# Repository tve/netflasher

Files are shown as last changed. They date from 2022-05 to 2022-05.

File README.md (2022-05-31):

NetFlasher2 - Emit a flash when a bird hits a net
================================================

The NetFlasher2 is a simple circuit to flash an LED when a bird hits a net and is used
in experiments to determine which window coverings are best to deter birds from flying
into them.

The netflasher detects when a bird hits a net using a vibration sensing switch.
It then briefly turns on a bright LED which is placed in the viewfield of a camera
recording the experiment.
This provides an unmistakable "hit" signal.

Instructions
------------

- Use micro-USB cable to power the netflasher (uses <80mA)
- The flashlight lights for 200ms when the vibration sensor is triggered
- After triggering, the flash is locked-out for 10s
- Tiny orange LED: slow (2s) = ready; fast (200ms) = 10s lock-out
- Red LED: vib sw detected (always active, even during lock-out)
- Green LED: display sensitivity (blink 1x/2x/3x/4x), 1=most, 4=least
- Blue sw:
  - first press: display sensitivity & reset lock-out
  - press again within 2s: change sensitivity (1/2/3/4)
- White sw next to microcontroller: program mode (cut power to exit)

Circuit Notes
-------------

### Net motion detector

- Vibration detection switch "SW-18010" https://www.adafruit.com/product/1766
- Sensitivity is adjusted by requiring toggles in multiple 10ms windows: sensitivity 1
  requires just one toggle, 2 requires toggles in 2x 10ms within 100ms of one-another,
  3 requires toggles in 2^2 = 4x 10ms intervals, 4 requires 8x 10ms intervals 

### Sensitivity switch

- Pushbutton to change sensitivity
- On-board sensitivity indicator LED (1, 2, 3, or 4 flashes)

### High power Cree LED

- Amber 5mm LED: C503B-ABS, 4430mcd @20mA, 40mA max continuous
- drive using 2N4401 w/82Ω -> ~40mA

### High power "flash" LED

(Not used due to size concerns)

- Wire-up raw flashlight LED
  - 135mA@2.8V=1/3W
  - 220mA@2.85V=0.6W
- 2N4401: 600mA max
  - resistor emitter-ground: 10Ω->1W flash
- On-board indicator LED
- To disassemble flashlight:
  - pull zoom ring hard and unscrew, remove driver
  - remove btn cap, punch btn through alum housing

Arduino
-------

To use `arduino-cli` install according to first post:
- https://forum.pjrc.com/threads/53548-Arduino-CLI-Alpha-Release-Teensy-Support
Instead of `arduino-cli core install teensy:avr` run:
- `arduino-cli core update-index`
- `arduino-cli core install teensy:arm`

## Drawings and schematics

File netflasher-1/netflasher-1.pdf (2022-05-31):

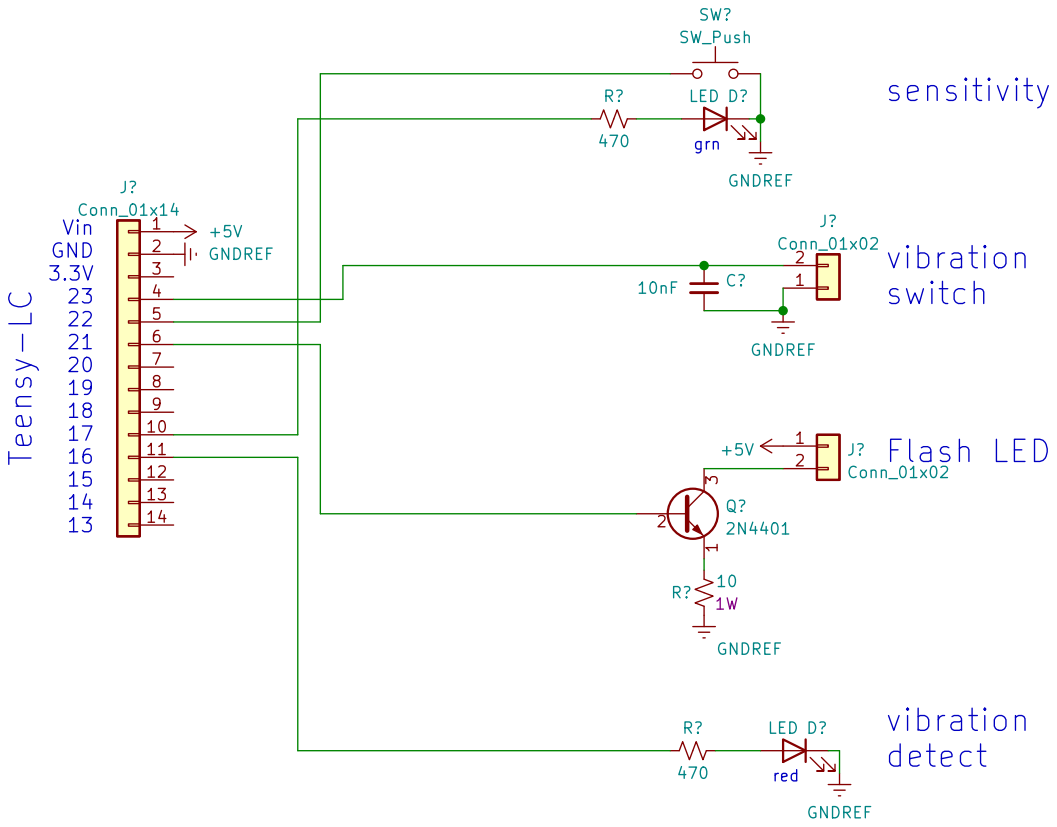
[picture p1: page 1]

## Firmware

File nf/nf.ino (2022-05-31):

#define codename "Net-Flasher"
#define codedate " 2022-0524 "

#include <EEPROM.h>
#include <Bounce.h>
typedef unsigned int u_int32;

const int vibSensePin = 23;
//Bounce vibSense = Bounce(vibSensePin, 10);
const int senseBtnPin = 22;
Bounce senseBtn = Bounce(senseBtnPin, 20);
const int flashEn = 21;
const int detectLed = 16;
const int senseLed = 17;
const int actLed = 13;
const int senseEE = 4;       // eeprom location
const int senseMax = 4;      // max vibration count value
const int flashDur = 200;    // flash duration in ms
int senseSet = 0;            // read from eeprom, vibration count setting
int senseCnt = 0;            // number of LED flashes to output (x2)
u_int32 senseAt = 0;         // last time the LED was updated
u_int32 senseBtnAt = 0;      // last time the button was pressed
volatile int vib = 0;        // set to 1 by interrupt handler
int vibCnt = 0;              // vibration count
int vibState = 0;            // digitalRead result

u_int32 flashAt = -60*1000;  // last time the flash was lit
u_int32 detectAt = -60*1000; // last time the detect LED was lit
u_int32 vibAt = 0;           // last time the detect LED was lit
u_int32 actAt = 0;           // last time the activity LED was updated

void vibIntr() { vib = 1; }

void setup(void) {
  //Serial.begin(115200); // unnecessary on teensy
  Serial.println("\nHello!");

  pinMode(flashEn, OUTPUT);
  pinMode(detectLed, OUTPUT);
  pinMode(senseLed, OUTPUT);
  pinMode(actLed, OUTPUT);
  pinMode(vibSensePin, INPUT_PULLUP);
  pinMode(senseBtnPin, INPUT_PULLUP);

  digitalWrite(flashEn, LOW);
  digitalWrite(detectLed, HIGH);
  digitalWrite(senseLed, HIGH);
  digitalWrite(actLed, HIGH);

  Serial.println(" ");
  Serial.print(codename);
  Serial.print(codedate);

  delay(300);
  digitalWrite(detectLed, LOW);
  digitalWrite(senseLed, LOW);
  digitalWrite(actLed, HIGH);

  attachInterrupt(vibSensePin, vibIntr, FALLING);

  senseSet = EEPROM.read(senseEE);
  if (senseSet < 1 || senseSet > senseMax) senseSet = 1;
  if (Serial) {
    Serial.print("sensitivity = ");
    Serial.println(senseSet);
  }
}

// ================================================================================================

void loop() {
  // slow the loop down
  delay(10);
  int now = millis();

  // read sensitivity button and adjust
  if (senseBtn.update()) {
    if (senseBtn.fallingEdge()) {
      if (now - senseBtnAt < 2000) {
        senseSet++;
        if (senseSet > senseMax) senseSet = 1;
        if (Serial) {
          Serial.print("sensitivity = ");
          Serial.println(senseSet);
        }
        EEPROM.write(senseEE, senseSet);
      } else {
        flashAt = now-60*1000;
      }
      senseCnt = senseSet*2;
      senseBtnAt = now;
    }
  }

  // flash sense button LED to indicate sensitivity
  if (senseCnt > 0 && now - senseAt > 200) {
    digitalWrite(senseLed, !(senseCnt&1));
    senseCnt--;
    senseAt = now;
  }

  // read vibration sensor
  //int v = digitalRead(vibSensePin);
  //if (v == 0 && v != vibState) {
  if (vib) {
    vibCnt++;
    vibAt = now;
    vib = 0;
    if (Serial) {
      Serial.print("vibration = ");
      Serial.println(vibCnt);
    }
    if (vibCnt > 1<<(senseSet-1)) {
      digitalWrite(detectLed, HIGH);
      detectAt = now;
      if (now - flashAt > 10*1000) {
        digitalWrite(flashEn, HIGH);
        flashAt = now;
      }
    }
  }
  //vibState = v;
  if (now - vibAt > 100) vibCnt = 0; // reset vibration count
  if (now - detectAt > 1000) digitalWrite(detectLed, LOW);
  if (now - flashAt > flashDur) digitalWrite(flashEn, LOW);
  if (now - flashAt > 60*1000) flashAt = now-60*1000; // avoid blind time when rolling over

  u_int32 actDel = now - flashAt > 10*1000 ? 2000 : 200;
  if (now - actAt > actDel) {
    digitalWrite(actLed, !digitalRead(actLed));
    actAt = now;
  }
}
